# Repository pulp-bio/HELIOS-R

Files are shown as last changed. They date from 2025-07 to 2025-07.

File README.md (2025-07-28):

# HELIOS-R

## Handheld Embedded Laser diode Illumination for Optoacoustic – Ring shaped

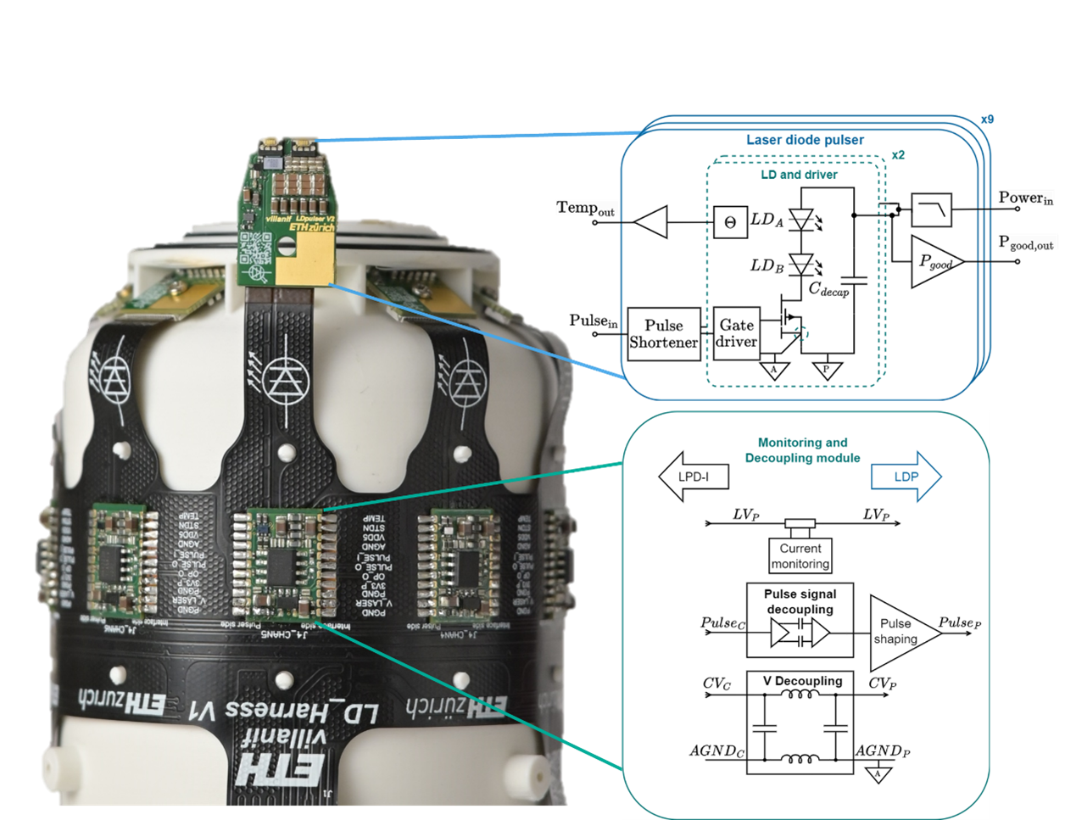
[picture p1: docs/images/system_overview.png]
System_overview


## Introduction

This repository contains the electronics design files for the HELIOS-R (Handheld Embedded Laser diode Illumination for Optoacoustic – Ring shaped) system. Helios-R is a high-current laser diode pulser array capable of delivering synchronized 100 ns light pulses at peak currents up to 2.88 kA at 22V, with a total light energy emission of up to 18 kW for up to 200 ns pulse widths.

The system drives a total of 144 laser diodes (9 pulser PCBs with 4 laser modules containing 4 laser diodes each) for optoacoustic imaging applications, featuring nanosecond-scale pulse generation with minimal electromagnetic interference in a compact, portable form factor.

## System Features

- **High-Current Pulsing**: 320 A per module, 2.88 kA total peak current capability
- **Nanosecond Timing**: Pulse shortening and pulse synchronization circuits for accurate timing control
- **Low EMI Design**: Advanced decoupling and filtering for minimal electromagnetic interference
- **Modular Architecture**: 9 independent pulser modules with monitoring and control

## System Architecture

The HELIOS-T electronics comprise four main PCB modules designed for optoacoustic imaging applications:

### Core Modules

1. **Laser Diode Pulser** (`ld_pulser`): High-current dual-channel GaN FET-based pulser with 4 laser diode modules, delivering 320 A at 22V pulse current. 
2. **Interconnect Harness** (`ld_harness`): Flexible PCB harness connecting all 9 pulsers with mechanical alignment and power distribution
3. **Monitoring & Decoupling** (`ld_monitoring_decoupling`): PI filter-based decoupling modules reduce EMI, featuring digital isolation and high-side current monitoring
4. **System Control** (`ld_system_control`): Interface PCB providing access to real-time monitoring of pulse duration, current consumption, and temperature



### Development & Testing

1. **Pulser Test Board** (`ld_pulser_testboard`): Standalone testing platform for pulser validation

## Repository Structure

This repository is organized as follows:

```text
HELIOS-R/
├── ld_pulser/                    # High-current laser diode pulser module
├── ld_system_control/           # Main system control unit
├── ld_monitoring_decoupling/    # Monitoring and signal conditioning
├── ld_harness/                 # Interconnection harness
├── ld_pulser_testboard/       # Standalone pulser test platform
├── shared/                   # Shared component libraries
│   └── lib/                 # Schematic and PCB component libraries
├── 3d_models/               # 3D models and mechanical assemblies
│   └── multiboard_assembly/ # Complete system 3D assembly
└── HELIOS_R.DsnWrk          # Altium Designer workspace file
```

each pcb module folder is structured as follows:
```
   ├── Hardware/                # PCB design files
   ├── Draftsman/               # Assembly and manufacturing drawings
   ├── Documentation/           # Schematics, assembly docs, and manufacturing files
   ├── Settings/                # Output job and BOM configurations
   └── <module_name>.PrjPcb     # Altium Designer PCB project file
```

## Key Specifications

- **Operating Voltage**: 22 V high-power rail
- **Operating Current**: Peak draw of 2A per module 
- **Peak Current**: 320 A per pulser module (Decoupled and filtered on each pulser module to obtain maximum draw of 2A per module)
- **Pulse Width**: 10-200 ns with 10 ns rising edge. Pulse shortening circuits shorten the pulse width by approximately 100ns
- **Pulse repetition Frequency**: Up to 10 kHz, depending on temperature and pulse width
- **PCB Specifications summary**:  
  - ld_pulser module: 6-layer, 1 mm thick with 70 µm copper planes and blind vias
  - ld_system_control: 6-layer, 1.2 mm thick
  - ld_harness: 2 layer flexible PCB
  - ld_monitoring_decoupling: 4-layer, 1 mm thick
- **EMI Suppression**: >120 dB attenuation (150 kHz - 280 MHz) via PI filtering
- **Decoupling Network**: 60 capacitors per module (47 nF, 2.2 µF, 10 µF stages)

## Getting Started

### Prerequisites for Development

- Altium Designer (recommended version 24.0 or later)

### Viewing the Design Files

1. **Open the workspace**:

   ```text
   Open HELIOS_R.DsnWrk in Altium Designer
   ```

2. **Navigate the projects**:
   - Each subsystem is organized as a separate Altium project
   - Hardware files contain schematics (.SchDoc) and PCB layouts (.PcbDoc)
   - Draftsman files contain assembly drawings and other information (.PCBDwf)

3. **Generate documentation**:
   - Use the provided OutJob files in each Settings folder
   - Generate PDFs, Gerber files, and BOMs as needed

## Manufacturing and Assembly

### PCB Fabrication

Each module includes complete manufacturing data:

- **Gerber Files**
- **Drill Files**
- **Pick & Place**: Component placement data for assembly
- **Bill of Materials (BOM)**

## Documentation

Comprehensive documentation is generated for each module:

- **Schematics**: Complete electrical schematics in PDF format
- **<project>_FULL_DOC.pdf**: Schematic, Fabrication and assembly instructions and component placement
- **Manufacturing Files**: fabrication and assembly data packages
- **BOMs**: Bill of materials with supplier information

Access documentation in the `Documentation/` folder of each project.

## Testing and Validation

Using the Pulser test board, pulsers can be tested individually by connecting them with a standard 18 pin, 0.5 mm pitch FPC cable.

## Safety Considerations

⚠️ **WARNING**: This system delivers extremely high energy light pulses. The system can only be operated in a laser-safe environment by safety-trained personnel. Exercise extreme caution and always follow safety protocols.
Please take note of the limitation of liability below [LIMITATION OF LIABILITY](#Limitation-of-Liability)

## Usage

1. connect a 22V, minimum 2A power supply (higher current required for faster pulse rates) to the banana plugs J6 and J5 on the back of the System Control module
2. Connect a 5V power supply to screw connector J10
3. Connect a signal generator (50 ohm, V_low = 0V, V_high = 5V) to the SMA connector J9 on the System Control module
4. Set a pulse width of 110 ns - 300 ns (the pulse width is shortened by approximately 100 ns by the pulse shortening circuit)
5. Set the pulse repetition frequency

The system can operate with a Laser diode supply voltage of up to 24V. It is reccomended to first enable the 5V power supply, then the Laser diode supply. 

## Contributing

This is an open hardware project. Contributions are welcome in the form of:

- Design improvements and optimizations
- Documentation enhancements
- Bug reports and fixes

## License

This project is released the Solderpad v0.51 open hardware license. See individual license files for specific terms:

- **Hardware Design Files**: Solderpad v0.51 (`SHL-0.51`) (see `LICENSE`)
- **Documentation and images**: Creative Commons Attribution 4.0 International License (`CC-BY-4.0`) (see `docs/LICENSE_CC`):

## Authors and Acknowledgments

The HELIOS-R PCB System was developed by the IIS laboratory at ETH Zurich by Federico Villani (System architecture, simulation, design and layout), based on requirements and the concept of handheld optoacoustic imaging by Xiang Liu and Prof. Daniel Razansky. 

The PCB system is part of a wider effort, the paper **Laser diode-based large-scale compounding handheld volumetric optoacoustic tomography**, with following summarized contributions (for the full list of contributions, please refer to the paper): 

- **Xiang Liu**:  Conceptualization, methodology, investigation, experimentation, software & data analysis, visualization, writing
- **Federico Villani**: PCB system design, methodology, investigation, writing
- **Isaac Esteban Varela**: Software & data analysis
- **Xuyang Chang** & **Baoyuan Zhang**: Investigation, experimentation
- **Andrea Cossettini**: Investigation, writing
- **Xose Luis Dean-Ben**: Software & data analysis, writing  
- **Luca Benini** & **Daniel Razansky**: Conceptualization, project administration, supervision, writing

```
@article{liuHandheldEmbeddedLaserDiode,
  title = {Handheld {{Embedded Laser-Diode Illumination Optoacoustic System}} for {{Real-Time 3D Angiography}} of {{Deep Tissues}}},
  author = {Liu, Xiang and Villani, Federico and Esteban, Isaac and Chang, Xuyang and Zhang, Baoyuan and Cossettini, Andrea and {De{\'a}n-Ben}, Xos{\'e} Lu{\'i}s and Benini, Luca and Razansky, Daniel},
  journal = {Laser \& Photonics Reviews},
  volume = {n/a},
  number = {n/a},
  pages = {e01006},
  issn = {1863-8899},
  doi = {10.1002/lpor.202501006},
  urldate = {2025-07-28},
  copyright = {{\copyright} 2025 The Author(s). Laser \& Photonics Reviews published by Wiley-VCH GmbH},
  langid = {english},
  keywords = {Compact,Handheld,Laser diode,Low cost,Nir wavelength,Optoacoustic Tomography,Photoacoustic,Vasculature}
}

```

Pictures of the system by: Federico Villani, Sergei Vostrikov, Xiang Liu.

## Contact and Support

For technical questions or design collaboration inquiries:

- Open an issue in this repository for technical discussions
- Contact us for collaboration opportunities

## Limitation of Liability

In no event and under no legal theory, whether in tort (including negligence), contract, or otherwise, unless required by applicable law (such as deliberate and grossly negligent acts) or agreed to in writing, shall any Contributor be liable to You for damages, including any direct, indirect, special, incidental, or consequential damages of any character arising as a result of this License or out of the use or inability to use the Work (including but not limited to damages for loss of goodwill, work stoppage, computer failure or malfunction, or any and all other commercial damages or losses), even if such Contributor has been advised of the possibility of such damages.

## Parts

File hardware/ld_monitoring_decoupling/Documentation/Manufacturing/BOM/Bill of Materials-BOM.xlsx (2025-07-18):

Line # | Name | Description | Designator | Footprint | LibRef | Supplier 1 | Supplier Part Number 1 | Quantity
 | 0 | RES SMD 0OHM 0.1% 1/20W 0201 | R4, R5 | RES 0201_0603 | ERJ-1GN0R00C | Mouser | 667-ERJ-1GN0R00C | 2
 | 0 | RES SMD 0OHM 1/10W 0402 | R7, R8 | RES 0402_1005 | ERJ-S020R00X | Mouser | 667-ERJ-S020R00X | 2
 | 0.1uF | CAP CER 0.1UF 35V X5R 0201 | C1, C2, C9, C10 | CAP 0201_0603 | GRM033R6YA104ME14D | Mouser | 81-GRM33R6YA104ME14D | 4
 | 1 kOhms @ 100 MHz | FERRITE BEAD 1K OHM 0603 1LN | FB1, FB2, FB3, FB4 | FER 0603_1608 | BLM18SP102SH1D | DigiKey | 490-BLM18SP102SH1DCT-ND | 4
 | 1uF | CAP LOW L CER 1UF 6.3V X7T 0204 | C4, C5, C6, C7, C13 | FP-LLL152-0_2-MFG | LLL152D70J105ME01D | Mouser | 81-LLL152D70J105ME01 | 5
 | 10k | RES SMD 10KOHM 0.1% 63mW 0402 | R3 | RES 0402_1005 | ERJ-1GNF1002C | Mouser | 667-ERA-2AEB103X | 1
 | 24 | RES SMD 24 OHM 1% 1/20W 0201 | R11 | RES 0201_0603 | ERJ-1GNF24R0C | Mouser | 667-ERJ-1GNF24R0C | 1
 | 200m | RES 0.2 OHM 1% 1/5W 0603 | R6 | STACKPOLE CSR0603 | RL0816S-R20-F | DigiKey | 408-1479-1-ND | 1
 | INA139NA_3K | IC Inamp high-side current monitor | U1 | SOT95P280X145-5N | INA139NA_3K | Mouser | 595-INA139NA/3K | 1
 | MAX22291CASA_V+ | IC Digital Isolator, 2CH | U2 | SOIC127P600X175-8N | MAX22291CASA_V+ | Mouser | 700-MAX22291CASA/V+ | 1
2 | 20 pF | CAP CER 20PF 50V C0G/NP0 0402 | C11, C12 | CAP 0402_1005 | GCM1555C1H200FA16D | DigiKey | 490-GCM1555C1H200FA16DCT-ND | 2
3 | 4.7uF | CAP CER 4.7UF 50V X6S 0805 | C3, C8, C14, C15 | CAP 0805_2012 | GRM21BC81H475KE11L | Mouser | 81-GRM21BC81H475KE1K | 4
18 | 4.99 k | RES SMD 4.99KOHM 0.1% 1/16W 0402 | R1, R2 | RES 0402_1005 | ERA-2AEB4991X | DigiKey | 10-ERA-2AEB4991XCT-ND | 2
23 | 4.99 k | RES SMD 4.99 kOHM 1% 1/20W 0201 | R9, R10 | RES 0201_0603 | ERJ-1GNF4991C | Mouser | 667-ERJ-1GNF4991C | 2
27 | SN74LVC1G08YZPR | IC Single 2-Input Positive-AND Gate, YZP0005ADAD, LARGE T&R | U3 | YZP0005ADAD | SN74LVC1G08YZPR | Mouser | 595-SN74LVC1G08YZPR | 1

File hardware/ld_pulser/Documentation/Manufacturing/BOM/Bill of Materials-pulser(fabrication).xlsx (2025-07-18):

Line # | Name | Description | Designator | Footprint | LibRef | Supplier 1 | Supplier Part Number 1 | Quantity
1 | 0.1uF | CAP CER 0.1UF 35V X5R 0201 | C1, C3, C5, C6, C7, C15 | CAP 0201_0603 | GRM033R6YA104ME14D | Digi-Key | 490-10431-1-ND | 6
2 | 20 pF | CAP CER 20PF 50V C0G/NP0 0402 | C2 | CAP 0402_1005 | GCM1555C1H200FA16D | Digi-Key | 490-GCM1555C1H200FA16DCT-ND | 1
3 | 10uF | CAP CER 10UF 25V X5R 0603 | C4, C13, C14, CC_1_1, CC_1_2, CC_1_3, CC_1_4, CC_1_5, CC_1_6, CC_2_1, CC_2_2, CC_2_3, CC_2_4, CC_2_5, CC_2_6 | CAP 0603_1608 | ZRB18AR61E106ME01L | Mouser | 81-ZRB18AR61E106ME1L | 15
4 | 2.2 µF | CAP CER 2.2UF 50V X5R 0603 | C_1_8, C_2_8, CB_1_1, CB_1_2, CB_1_3, CB_1_4, CB_1_5, CB_1_6, CB_1_7, CB_1_8, CB_1_9, CB_1_10, CB_1_11, CB_1_12, CB_2_1, CB_2_2, CB_2_3, CB_2_4, CB_2_5, CB_2_6, CB_2_7, CB_2_8, CB_2_9, CB_2_10, CB_2_11, CB_2_12 | CAP 0603_1608 | GRM188R61H225KE11D | Mouser | 81-GRM188R71A225KE15 | 26
5 | NFM15PC474R0J3D | CAP Feed Through, 470 nF, 6.3V, 2A, 3 Pin(s) | C_1_9, C_2_9 | FP-NFM15-0_05-MFG | NFM15PC474R0J3D | Mouser | 81-NFM15PC474R0J3D | 2
6 | 47 nF | CAP CER 47 nF, 50V, 20% X7R 0204 | C_1_10, C_2_10, CA_1_1, CA_1_2, CA_1_3, CA_1_4, CA_1_5, CA_1_6, CA_1_7, CA_1_8, CA_1_9, CA_1_10, CA_1_11, CA_1_12, CA_1_13, CA_1_14, CA_1_15, CA_2_1, CA_2_2, CA_2_3, CA_2_4, CA_2_5, CA_2_6, CA_2_7, CA_2_8, CA_2_9, CA_2_10, CA_2_11, CA_2_12, CA_2_13, CA_2_14, CA_2_15 | CAPC0510X35N | CGAEA1X7R1H473M030BC | Mouser | 810-CGAEA1X7R1H473M0 | 32
7 | 1uF | CAP LOW L CER 1UF 6.3V X7T 0204 | C_1_11, C_2_11 | FP-LLL152-0_2-MFG | LLL152D70J105ME01D | Mouser | 81-LLL152D70J105ME01 | 2
8 | 33nF | CAP LOW L CER 33nF 25V X5R 0102 | C_1_12, C_2_12 | FP-LLL03T-0_03-IPC_C | LLL03TR61E333KE01 | Mouser | 81-LLL03T61E333KE01L | 2
9 | SPL_S4L90A_3_A01 | Diode Laser | D_1_1, D_1_2, D_2_1, D_2_2 | SPLS4L90A_3A01 | SPL_S4L90A_3_A01 | Mouser | 720-SPLS4L90A3A01 | 4
10 | APG0603SEC-E-TT | Diode LED RED 10 mA @ 1.93 V lv=40 | LED1 | APG0603SECETT | APG0603SEC-E-TT | Mouser | 604-APG0603SECETT | 1
11 | APG0603VBC-A1-5MAV | Diode LED BLUE 10 mA @ 2.9 V lv=60 | LED2 | APG0603SECETT | APG0603VBC-A1-5MAV | Mouser | 604-APG0603VBCA15MAV | 1
12 | APG0603ZGC-5MAV | Diode LED GREEN 5 mA @ 2.85 V lv=80(?) | LED3 | APG0603SECETT | APG0603ZGC-5MAV | Mouser | 604-APG0603ZGC-5MAV | 1
13 | =Value | FERRITE BEAD 100 OHM 0603 1LN | FB1, FB2 | FER 0603_1608 | BLM18SP101SN1 | Mouser | 81-BLM18SP101SN1D | 2
14 | NFL18ZT506H1A3D | LC Filter | FL_1_1, FL_2_1 | NFL18ST107H1A3D | NFL18ZT506H1A3D | Mouser | 81-NFL18ZT506H1A3D | 2
15 | EPC2619ENGRT | Transistor eGaN | Q_1_1, Q_2_1 | EPC2619ENGRT | EPC2619ENGRT | Digi-Key | 917-EPC2619ENGRTCT-ND | 2
16 | 51 | RES SMD 51 OHM 1% 1/20W 0201 | R3 | RES 0201_0603 | ERJ-1GNF51R0C | Mouser | 667-ERJ-1GNF51R0C | 1
17 | 4.99 k | RES SMD 4.99KOHM 0.1% 1/16W 0402 | R2, R12 | RES 0402_1005 | ERA-2AEB4991X | Digi-Key | 10-ERA-2AEB4991XCT-ND | 2
18 | 470 | RES SMD 470 OHM 1% 1/20W 0201 | R1, R4 | RES 0201_0603 | ERJ-1GNF4991C_1 | Mouser | 667-ERJ-1GNF4700C | 2
19 | 1 M | RES SMD 1MOHM 1% 1/20W 0201 | R6 | RES 0201_0603 | ERJ-U01F1004C | Mouser | 667-ERJ-U01F1004C | 1
20 | 100k | RES SMD 100 kOHM 0.5% 1/20W 0201 | R7 | RES 0201_0603 | ERJ-1RHD1003C | Mouser | 667-ERJ-1RHD1003C | 1
21 | LM94023BITME_NOPB | IC temperature sensor | U1 | BGA4C40P2X2_81X81X68 | LM94023BITME_NOPB | Mouser | 926-94023bitME/NOPB | 1
22 | 4.99 k | RES SMD 4.99 kOHM 1% 1/20W 0201 | R9 | RES 0201_0603 | ERJ-1GNF4991C | Mouser | 667-ERJ-1GNF4991C | 1
23 | 2 | RES SMD 2 OHM 1% 1/20W 0201 | R_1_10, R_1_11, R_2_10, R_2_11 | RES 0201_0603 | ERJ-1GNJ2R0C | Mouser | 667-ERJ-1GNJ2R0C | 4
24 | MAX40007ANT+ | Operational Amplifier | U4 | BGA6C40P3X2_124X84X69 | MAX40007ANT+ | Mouser | 700-MAX40007ANT+T | 1
25 | 503480-1800 | Conn FPC 18 POS 0.5mm | J1 | 5034801800 | 503480-1800 | Mouser | 538-503480-1800 | 1
26 | SN74LVC1G08YZPR | IC Single 2-Input Positive-AND Gate, YZP0005ADAD, LARGE T&R | U2 | YZP0005ADAD | SN74LVC1G08YZPR | Mouser | 595-SN74LVC1G08YZPR | 1
28 | SN74LVC1G06YZPR | IC Single Inverter Buffer/Driver With Open-Drain Output, YZP0005ADAD, LARGE T&R | U7 | YZP0005ADAD | SN74LVC1G06YZPR | Mouser | 595-SN74LVC1G06YZPR | 1
29 | LMG1020YFFR | IC Pulser | U_1_6, U_2_6 | BGA6C40P2X3_86X126X62 | LMG1020YFFR | Mouser | 595-LMG1020YFFR | 2

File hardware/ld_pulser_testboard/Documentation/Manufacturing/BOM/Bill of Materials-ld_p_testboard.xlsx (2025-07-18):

Name | Description | Designator | Footprint | LibRef | Supplier 1 | Supplier Part Number 1 | Quantity | Line #
10 µF | CAP CER 10UF 100V X7S 1210 | C1, C2 | CAP 1210_3225 - 1MM | GRM32EC72A106ME05L | Digi-Key | 490-GRM32EC72A106ME05LCT-ND | 2 | 4
503480-2400 | Connector | J1 | 5034802400 | 503480-2400 | Mouser | 538-503480-2400 | 1 | 6
282834-2 | TERM BLK 2P SIDE ENT 2.54MM PCB | J2, J3, J9 | TE 282834-2 | 282834-2 | Digi-Key | A98333-ND | 3 | 9
1470510-1 | SMA Connector Jack, Female Socket 50 Ohm Through Hole Solder | J4, J5, J6, J8 | 5-1814832-1 | CMP-00606-1 |  |  | 4 | 8
M20-7820342 | CONN RCPT 3POS 0.1 GOLD PCB | J7 | HARWIN M20-7820345 | M20-7820342 | Digi-Key | 952-1783-ND | 1 | 5
51 | RES SMD 51 OHM 1% 1/20W 0201 | R1, R2 | RES 0201_0603 | ERJ-1GNF51R0C | Mouser | 667-ERJ-1GNF51R0C | 2 | 7
TPSM265R1V3SILR | 3-V TO 65-V INPUT, 100-MA, STEP- | U1 | FP-SIL0010C-MFG | TPSM265R1V3SILR | Mouser | 595-TPSM265R1V3SILR | 1
68000-102HLF | 2 Positions Header, Unshrouded Connector 0.100" (2.54mm) Through Hole Gold or Gold, GXT™ | X1, X2, X3, X6, X8 | 68000-102HLF | CMP-00100-3 | Arrow Electronics | 68000-102HLF | 5 | 1
68000-102HLF | 2 Positions Header, Unshrouded Connector 0.100" (2.54mm) Through Hole Gold or Gold, GXT™ | X4, X5, X7, X9 | 68000-102HLF | CMP-00100-3_1 | Arrow Electronics | 68000-102HLF | 4 | 2

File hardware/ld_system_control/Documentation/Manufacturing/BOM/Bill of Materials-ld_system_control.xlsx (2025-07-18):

Name | Description | Designator | Footprint | LibRef | Supplier 1 | Supplier Part Number 1 | Quantity | Line #
10 µF | CAP CER 10UF 100V X7S 1210 | C1, C2 | CAP 1210_3225 - 1MM | GRM32EC72A106ME05L | Digi-Key | 490-GRM32EC72A106ME05LCT-ND | 2 | 4
200528-0140 | FFC / FPC Board Connector, 1 mm, 14 Contacts, Receptacle, Easy-On 52207 Series, Surface Mount | J1 | 200528-0140 | 522071460 | Mouser | 538-52207-1460 | 1
503480-1800 | Conn FPC 18 POS 0.5mm | J2, J3 | 5034801800 | 503480-1800 | Mouser | 538-503480-1800 | 2
M20-7820342 | Header 3 Positions, Unshrouded Connector 0.100" (2.54mm) Through Hole Gold or Gold, GXT™ | J4, J8 | HARWIN M20-7820345 | M20-7820342 | DigiKey | 952-1783-ND | 2
CT3151-2 | Banana plug connector - Red | J5 | CT31510 | CT3151-2 | Mouser | 510-CT3151-2 | 1
CT3151-0 | Banana plug connector - Black | J6 | CT31510 | CT3151-0 | Mouser | 510-CT3151-0 | 1
1470510-1 | SMA Connector Jack, Female Socket 50 Ohm Through Hole Solder | J7, J9 | 5-1814832-1 | CMP-00606-1 |  |  | 2 | 8
282834-2 | TERM BLK 2P SIDE ENT 2.54MM PCB | J10 | TE 282834-2 | 282834-2 | DigiKey | A98333-ND | 1
WSL3637R0100DEA | current measurement Resistor | R1 | WSL3637R0100DEA | WSL3637R0100DEA | Mouser | 71-WSL3637R0100DEA | 1
51 | RES SMD 51 OHM 1% 1/20W 0201 | R2 | RES 0201_0603 | ERJ-1GNF51R0C | Mouser | 667-ERJ-1GNF51R0C | 1 | 7
TPSM265R1V3SILR | 3-V TO 65-V INPUT, 100-MA, STEP- | U1 | FP-SIL0010C-MFG | TPSM265R1V3SILR | Mouser | 595-TPSM265R1V3SILR | 1
68000-102HLF | Header 2 Positions , Unshrouded Connector 0.100" (2.54mm) Through Hole Gold or Gold, GXT™ | X1, X2, X4, X5 | 68000-102HLF | CMP-00100-3_1 |  |  | 4
68000-102HLF | Header 9*2 Positions, Unshrouded Connector 0.100" (2.54mm) Through Hole Gold or Gold, GXT™ | X6, X8 | TSW-109-07-G-D | 68000-102HLF |  |  | 2
68000-102HLF | Header 2 positions, Unshrouded Connector 0.100" (2.54mm) Through Hole Gold or Gold, GXT™ | X7 | 68000-102HLF | CMP-00100-3 |  |  | 1

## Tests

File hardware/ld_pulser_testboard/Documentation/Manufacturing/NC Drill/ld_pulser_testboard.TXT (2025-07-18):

M48
;Layer_Color=9474304
;FILE_FORMAT=4:4
METRIC,LZ
;TYPE=PLATED
T01F00S00C0.3000
T02F00S00C1.0200
T03F00S00C1.1000
T04F00S00C1.1000
T05F00S00C1.5000
T06F00S00C1.6000
T07F00S00C3.3000
%
T01
X002728Y000135
X002878
X002875Y000275
X002975
X003075
X003175
X003275
X003375
X00347246Y00026652
X00355746
X00364246
X00372746
X00381246
X00389746
X00398246
X00406746
X00415246
X00423746
X00432246
X00440746
X00449246
X00457746
X00466246
X00474746
X00483246Y00026701
X00488098Y0003368
Y0004218
Y0005068
Y0005918
Y0006768
Y0007618
Y0008468
Y0009318
Y0010168
X00505299Y000885
X00520299
X00535299
X00550299
X00542799Y000735
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

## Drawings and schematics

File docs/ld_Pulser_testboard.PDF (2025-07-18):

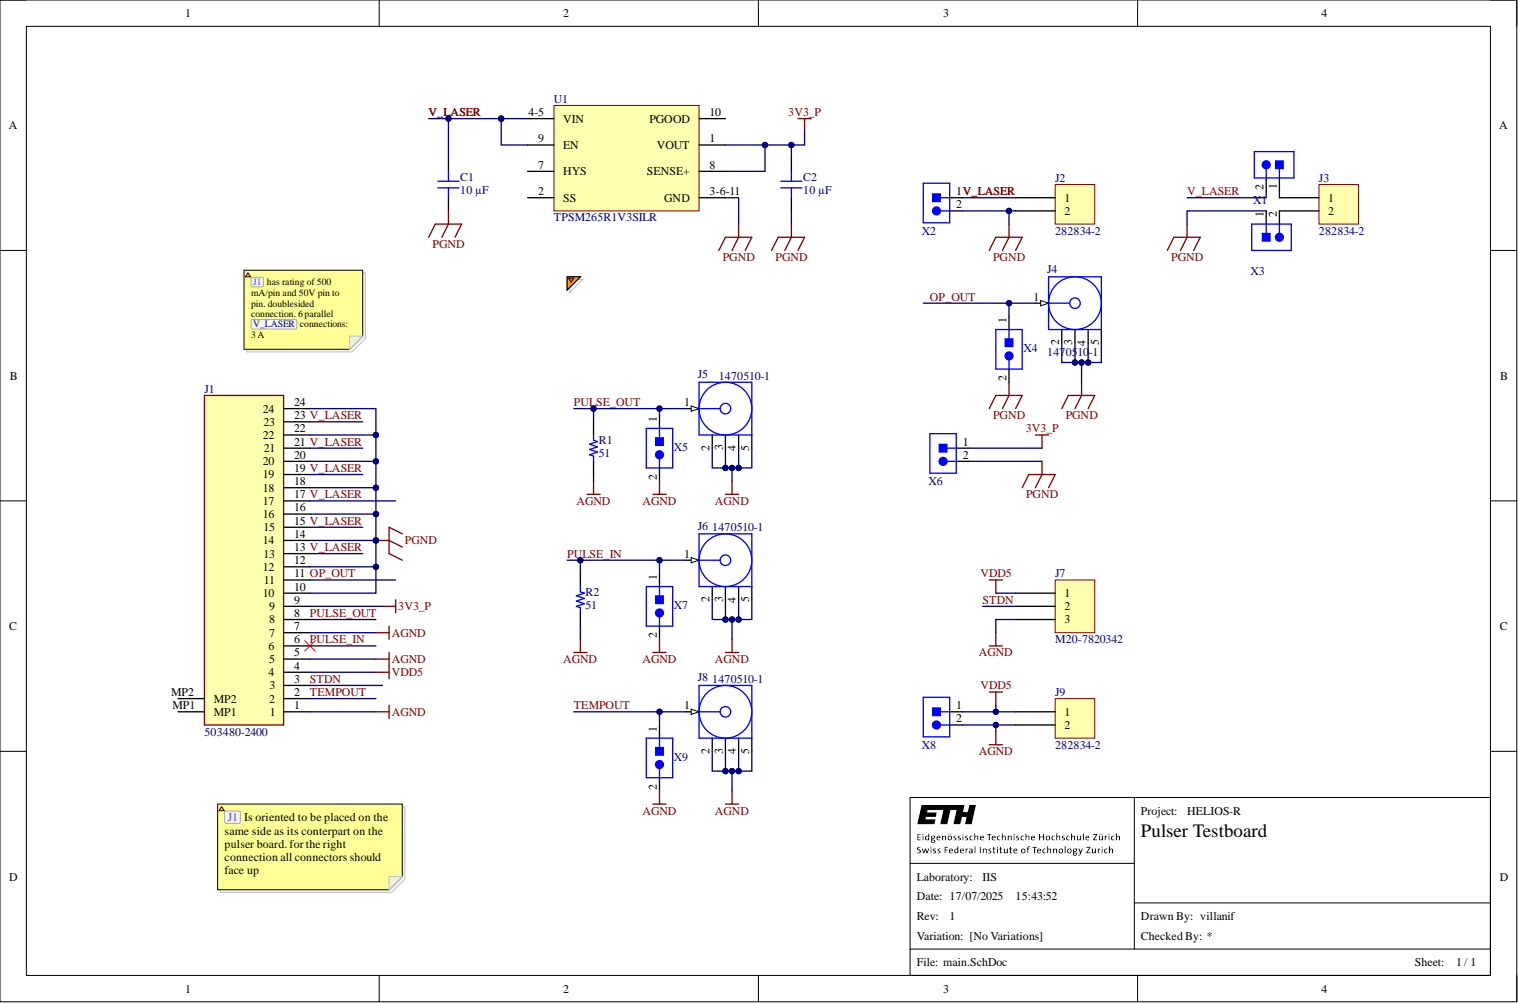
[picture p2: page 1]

2 3 2 2 | V _ L ASE R

2 1 2 0 | V _ L ASE R

1 9 1 8 | V _ L ASE R

1 7 | V _ L ASE R
1 6

1 3 1 2 | V _ L ASE

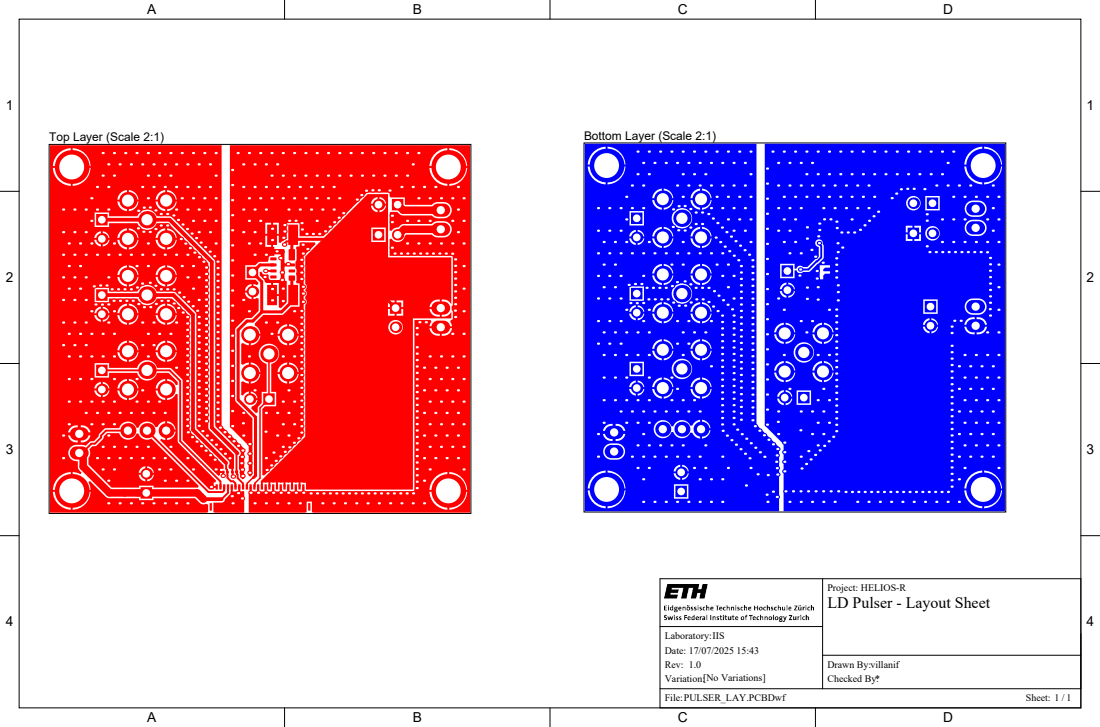
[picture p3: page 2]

Project: HELIOS-R
LD Pulser - Layout Sheet

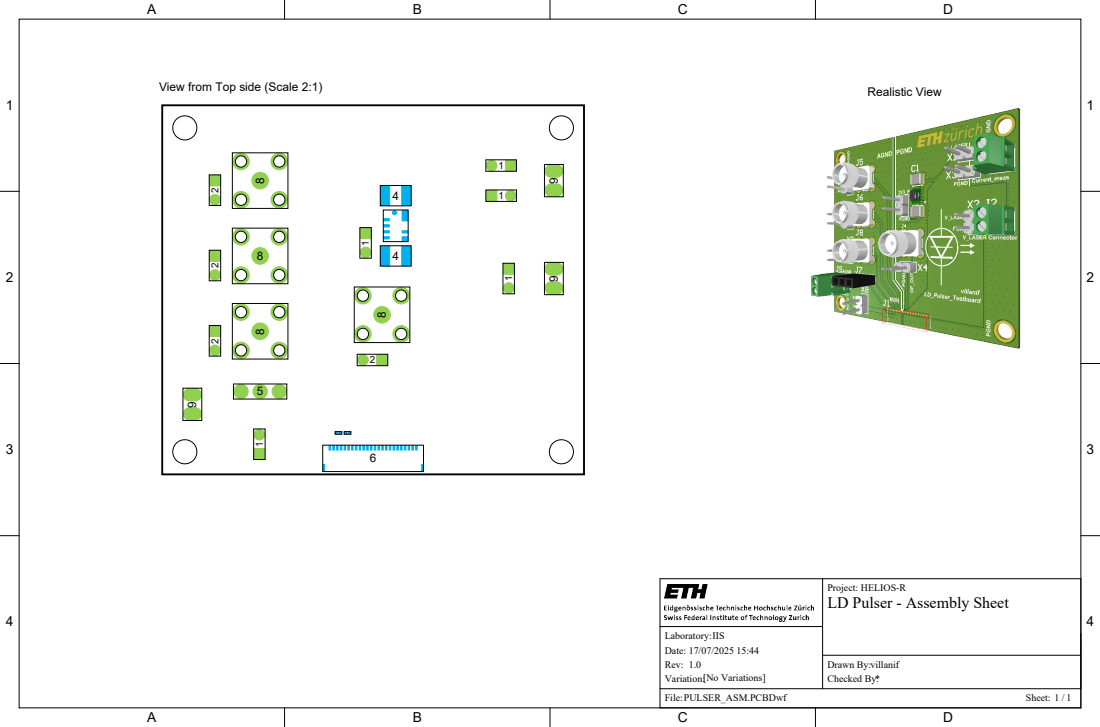
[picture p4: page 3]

View from Top side (Scale 2:1)

Project: HELIOS-R
LD Pulser - Assembly Sheet

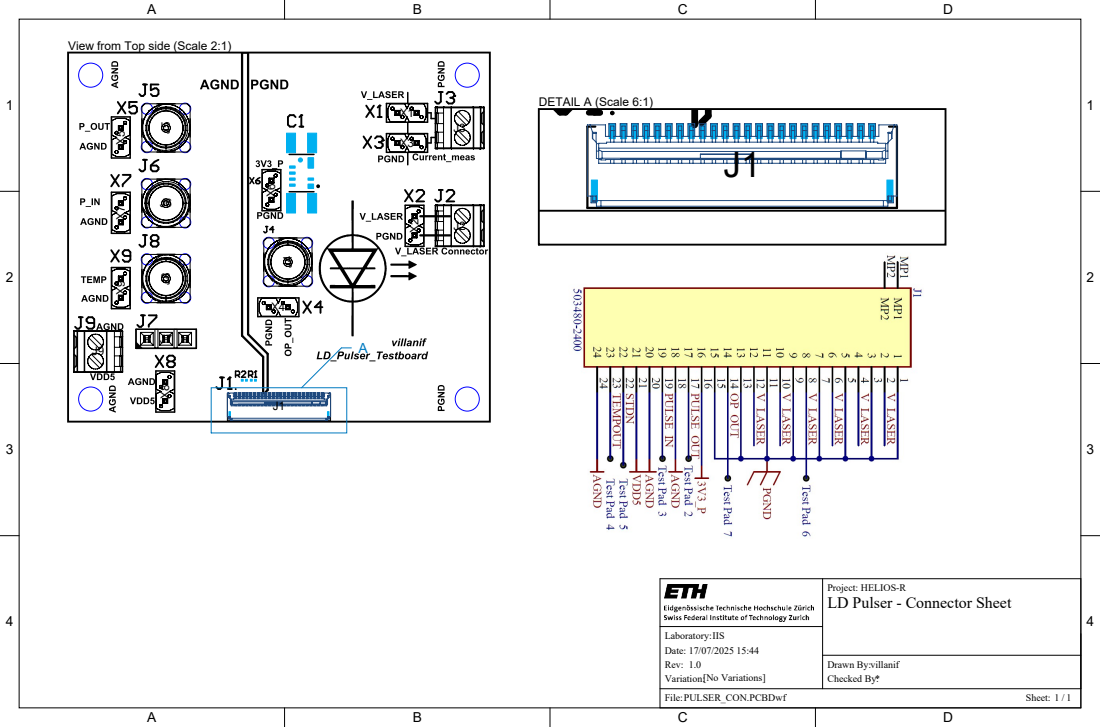
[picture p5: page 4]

View from Top side (Scale 2:1)

Project: HELIOS-R
LD Pulser - Connector Sheet

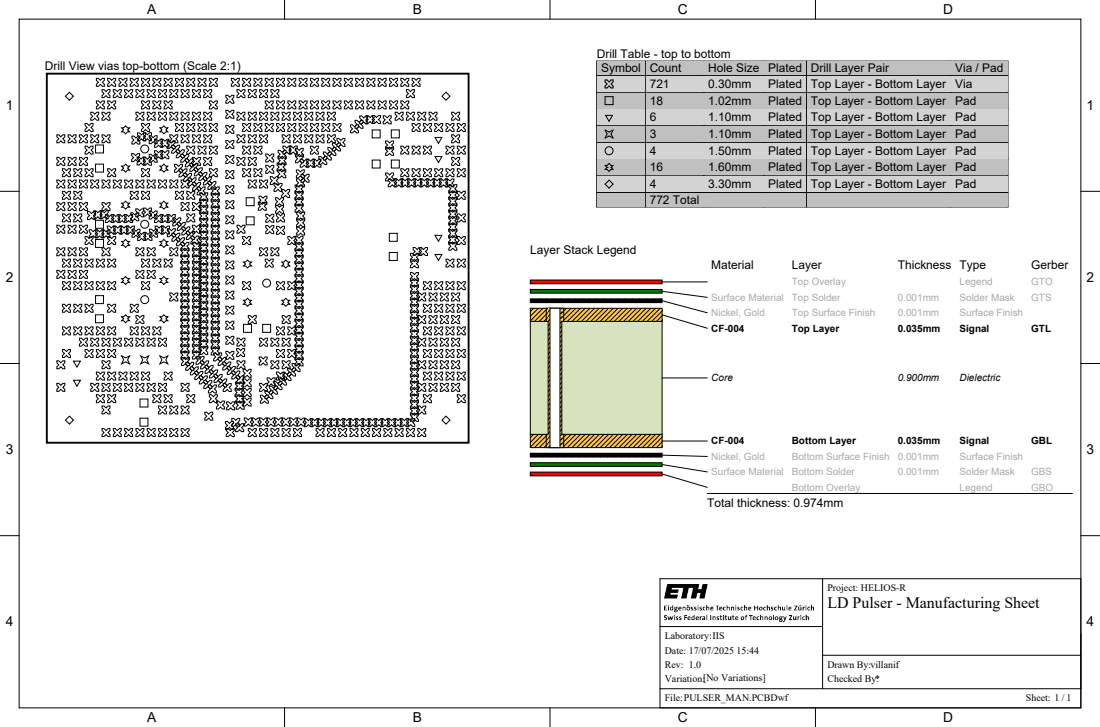
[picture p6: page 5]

Drill Table - top to bottom

Drill View vias top-bottom (Scale 2:1)

Symbol | Count | Hole Size | Plated | Drill Layer Pair | Via / Pad

721 | 0.30mm | Plated | Top Layer - Bottom Layer | Via
18 | 1.02mm | Plated | Top Layer - Bottom Layer | Pad
6 | 1.10mm | Plated | Top Layer - Bottom Layer | Pad
3 | 1.10mm | Plated | Top Layer - Bottom Layer | Pad
4 | 1.50mm | Plated | Top Layer - Bottom Layer | Pad
16 | 1.60mm | Plated | Top Layer - Bottom Layer | Pad
4 | 3.30mm | Plated | Top Layer - Bottom Layer | Pad
772 Total

Project: HELIOS-R
LD Pulser - Manufacturing Sheet

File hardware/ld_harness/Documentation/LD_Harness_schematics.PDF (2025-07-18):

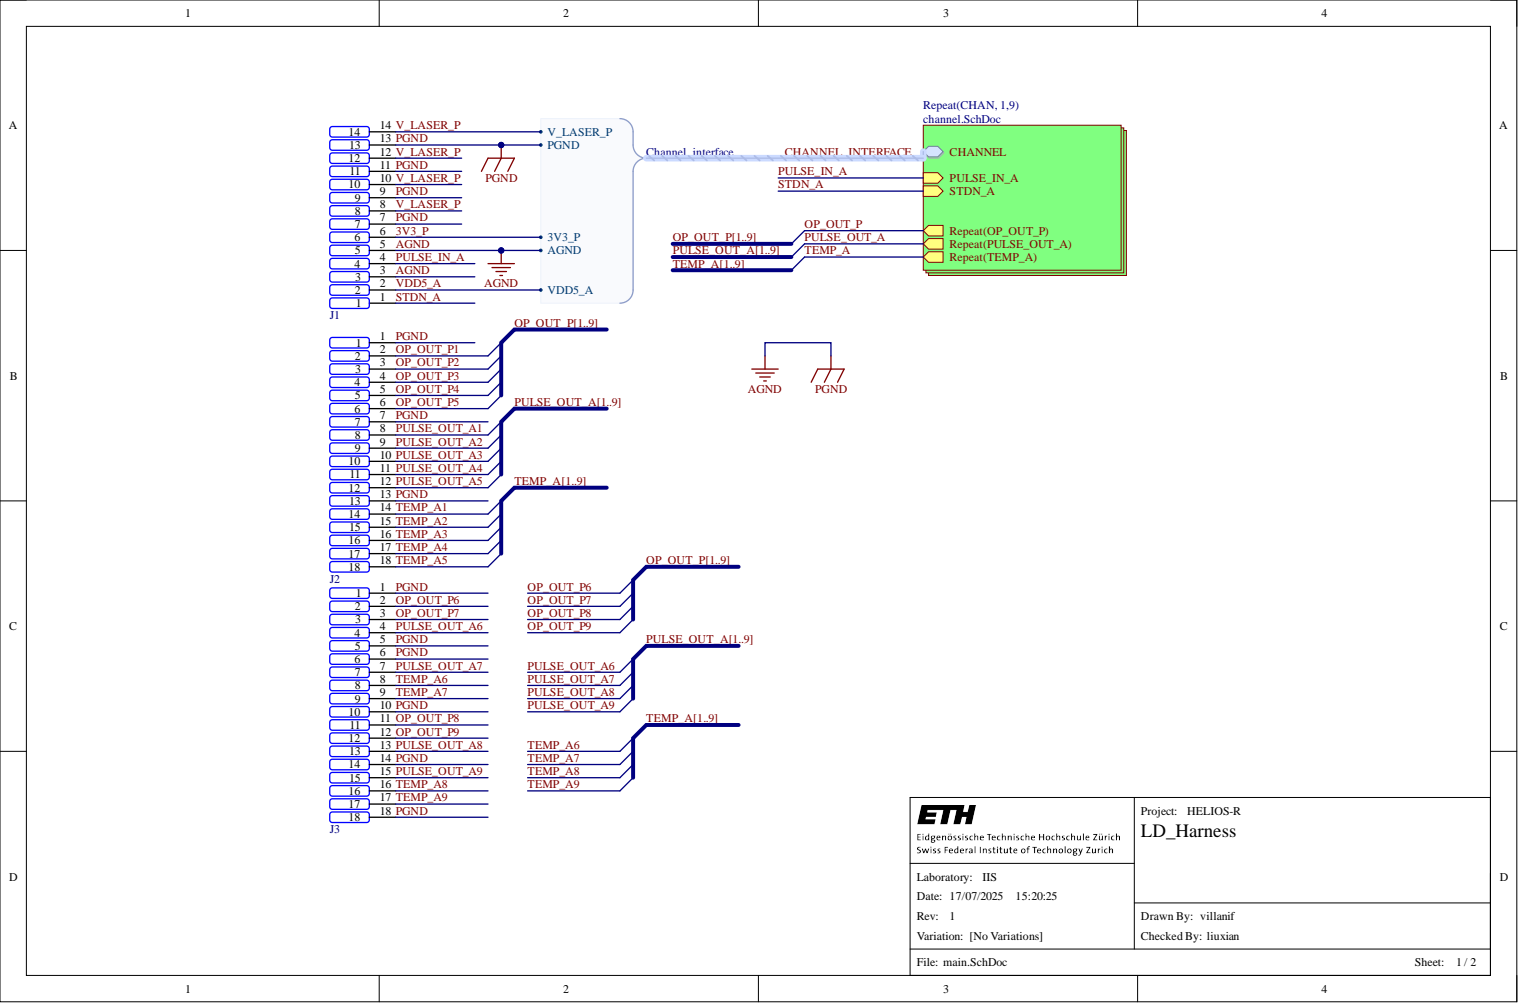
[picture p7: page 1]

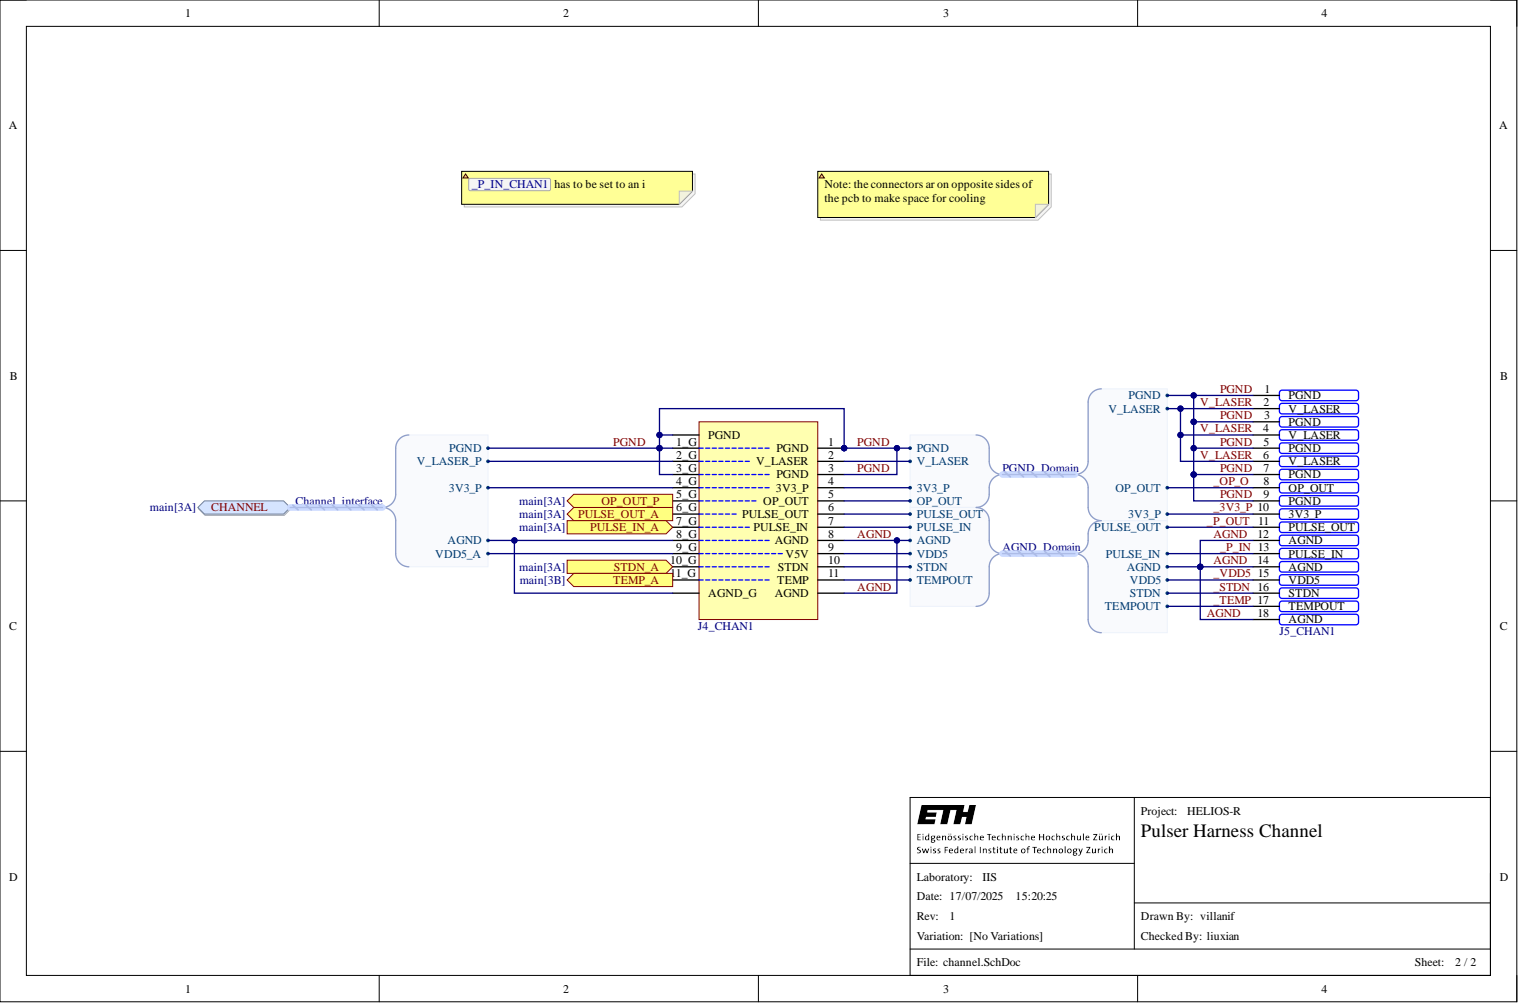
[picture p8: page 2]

_P_IN_CHAN1 has to be set to an i

Note: the connectors ar on opposite sides of
the pcb to make space for cooling

PGND

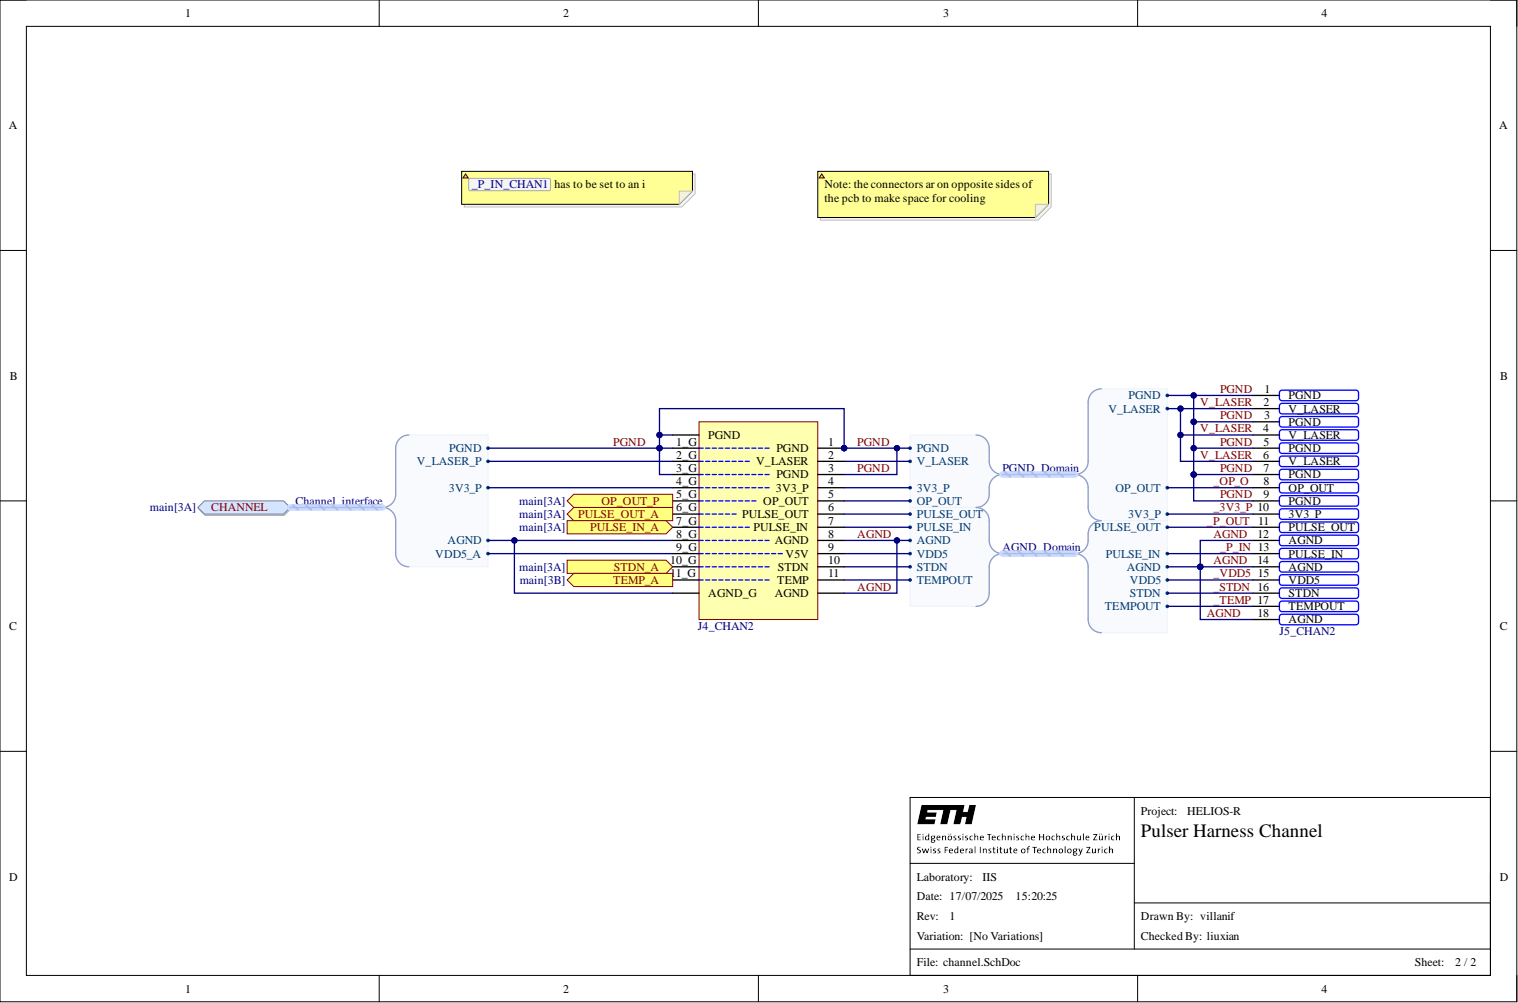
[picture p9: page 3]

_P_IN_CHAN1 has to be set to an i

Note: the connectors ar on opposite sides of
the pcb to make space for cooling

PGND

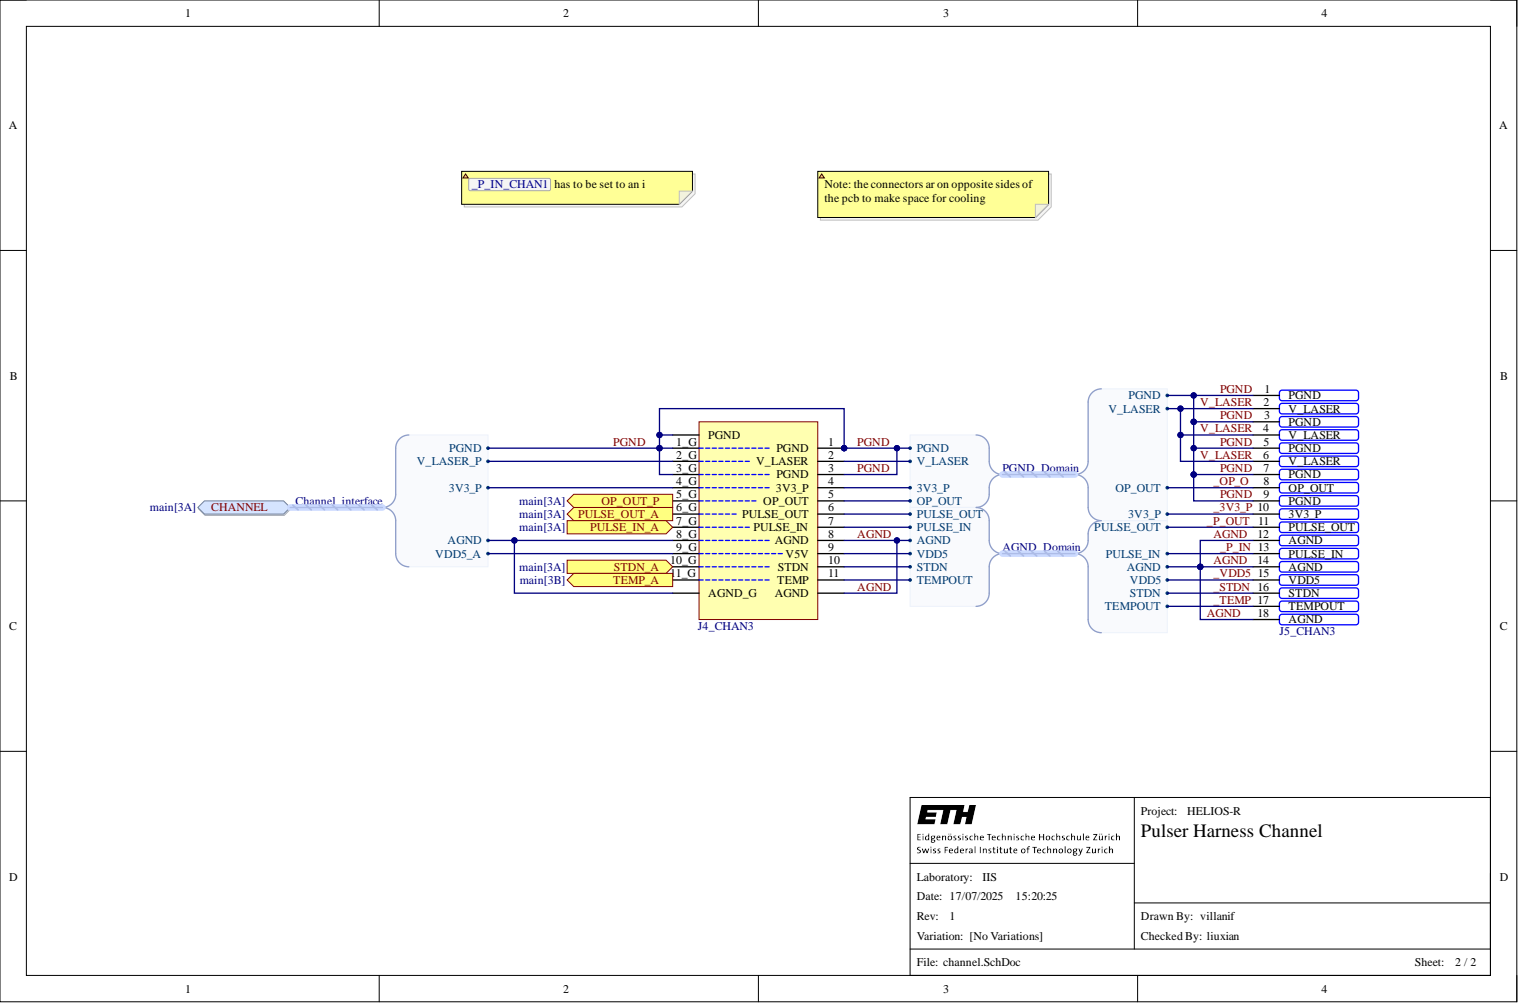
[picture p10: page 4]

_P_IN_CHAN1 has to be set to an i

Note: the connectors ar on opposite sides of
the pcb to make space for cooling

PGND

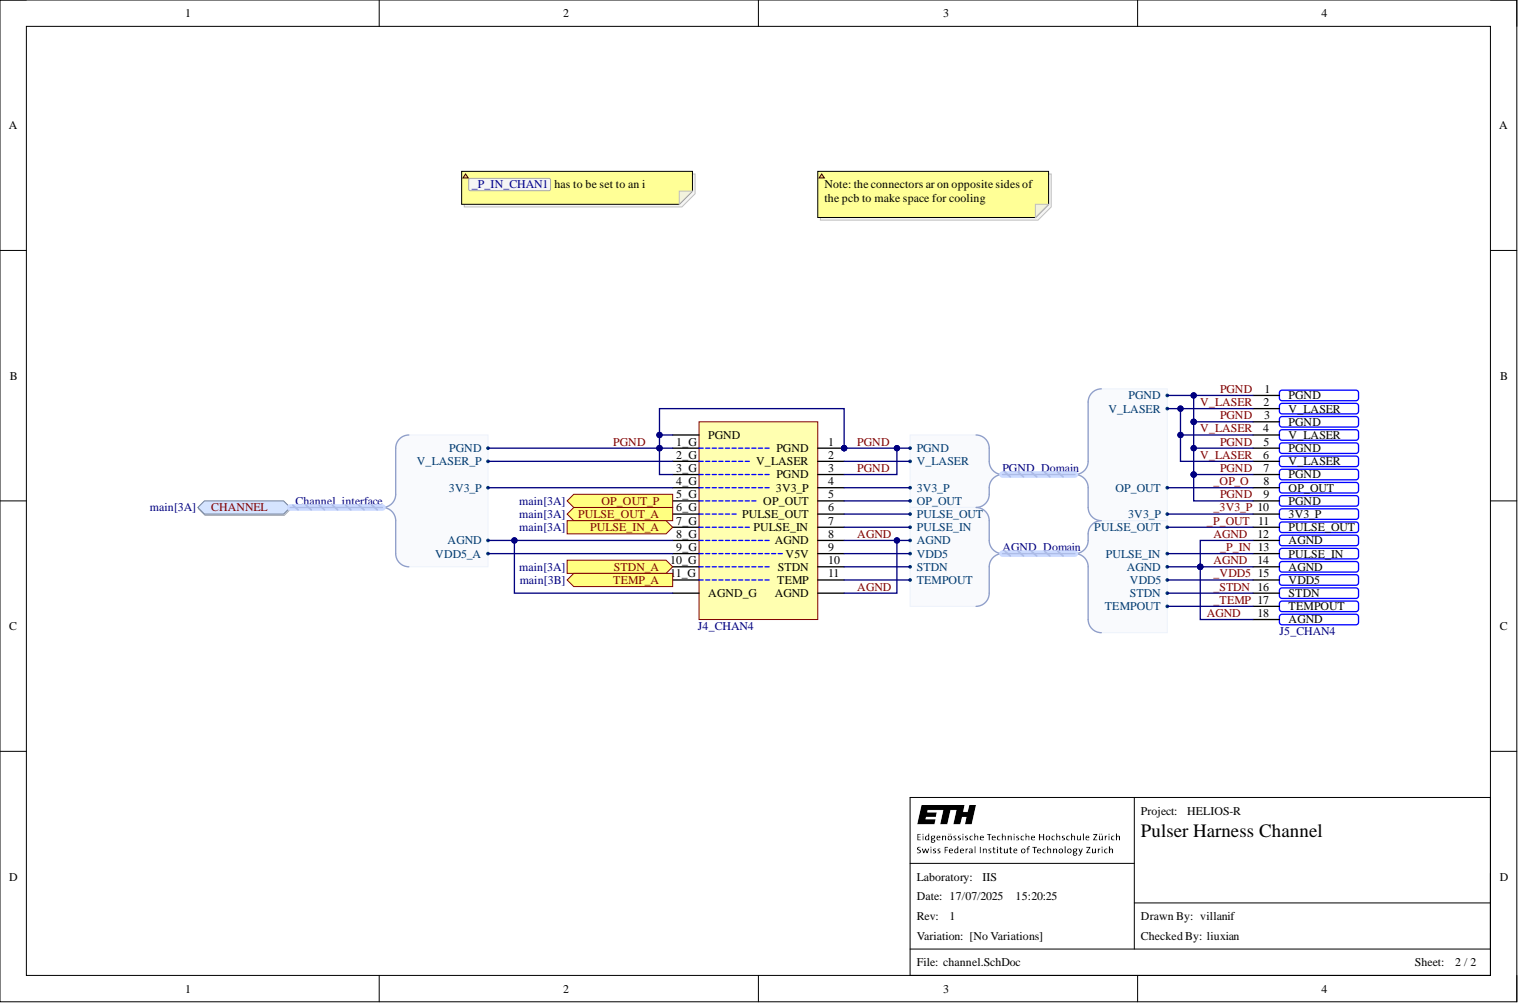
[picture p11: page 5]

_P_IN_CHAN1 has to be set to an i

Note: the connectors ar on opposite sides of
the pcb to make space for cooling

PGND

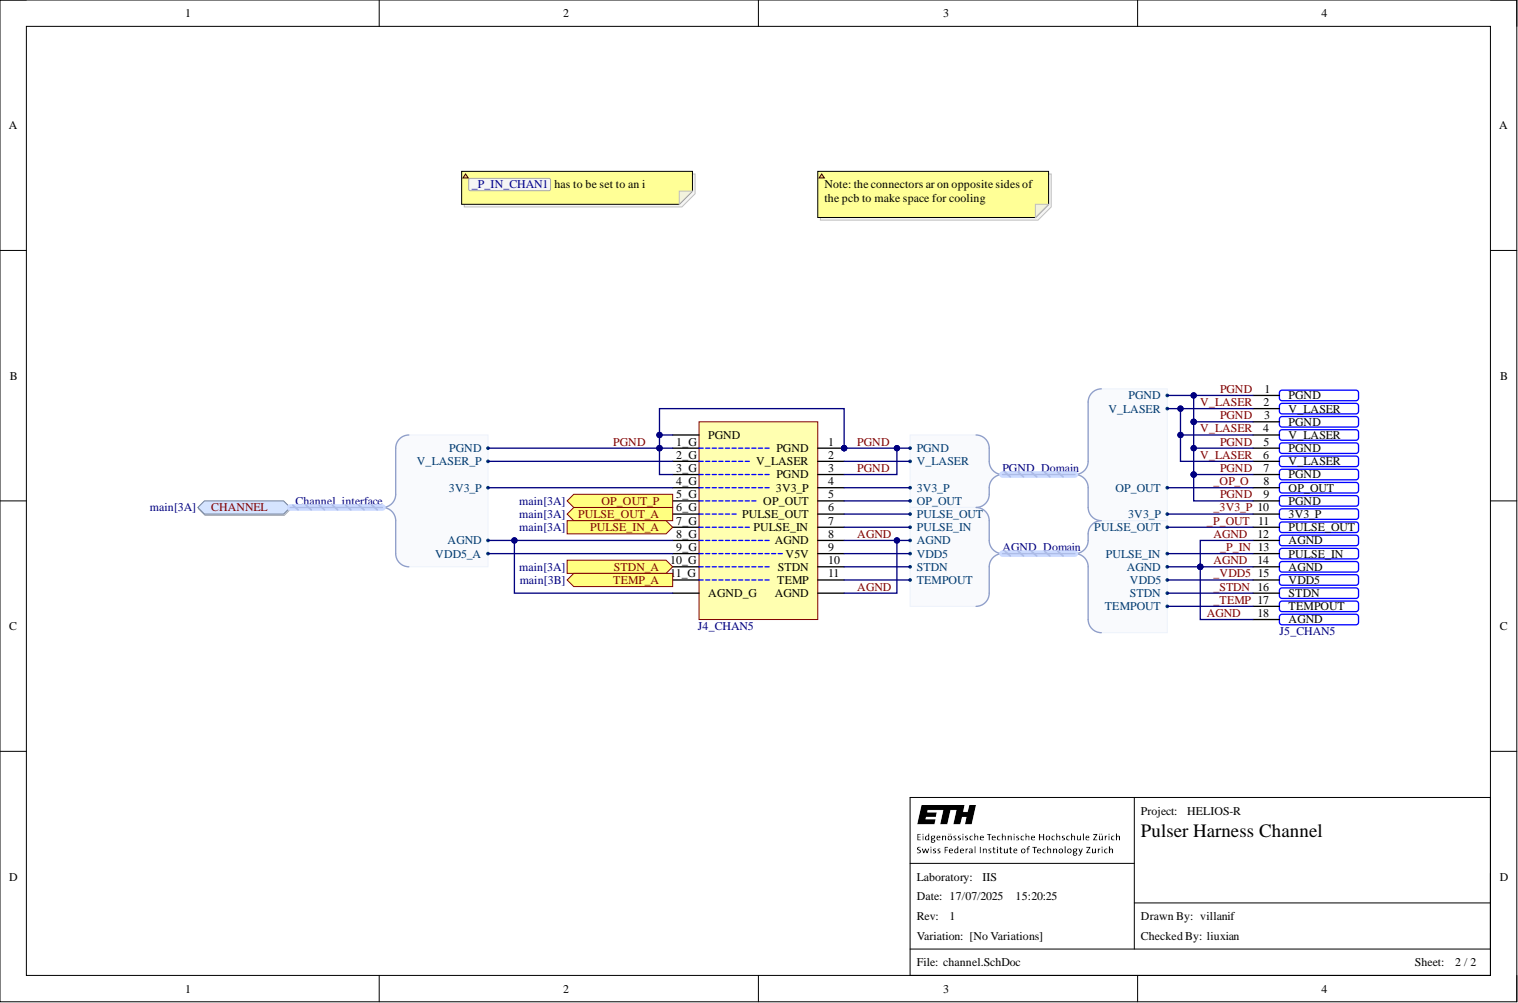
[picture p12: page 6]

_P_IN_CHAN1 has to be set to an i

Note: the connectors ar on opposite sides of
the pcb to make space for cooling

PGND

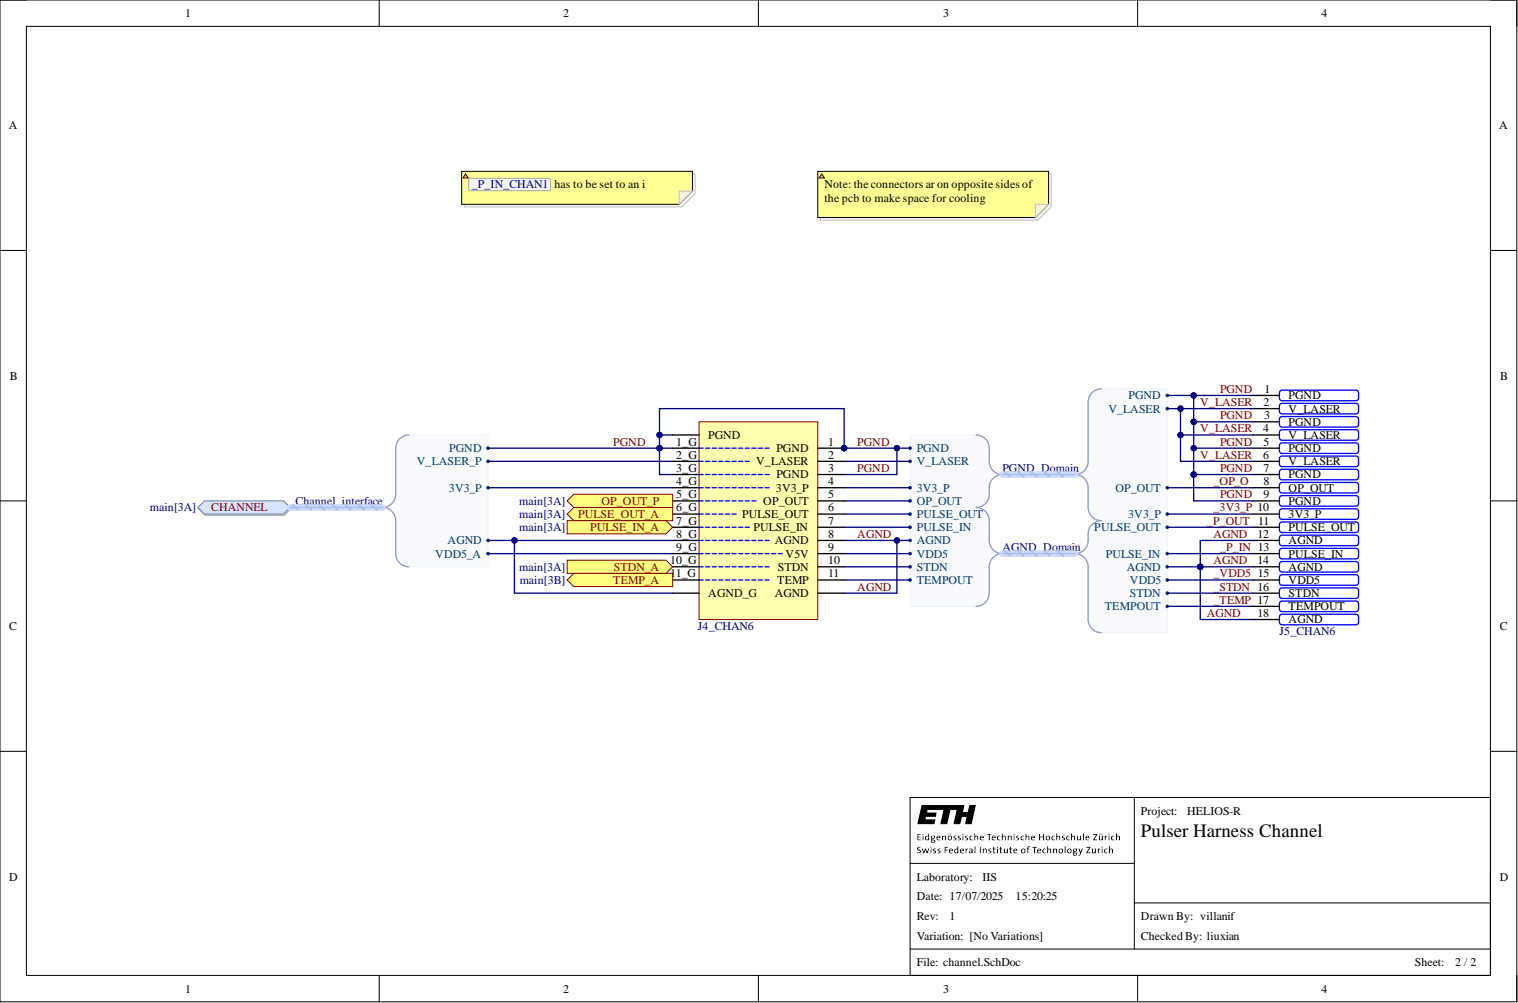
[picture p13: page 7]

_P_IN_CHAN1 has to be set to an i

Note: the connectors ar on opposite sides of
the pcb to make space for cooling

PGND


_P_IN_CHAN1 has to be set to an i

Note: the connectors ar on opposite sides of
the pcb to make space for cooling

PGND


_P_IN_CHAN1 has to be set to an i

Note: the connectors ar on opposite sides of
the pcb to make space for cooling

PGND


1 0

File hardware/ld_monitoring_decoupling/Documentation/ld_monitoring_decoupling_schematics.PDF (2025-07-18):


Requirements for digital isolator:
min pulse (unshortened) is 100 ns, max pulse 250ns
Specifications might be exceeded without causing extra
damage

power consumption of the whole board <10 mA
1 global to isolated high speed (PULSE)
1 global to isolated low speed (STDN)
Optional: 1 high-speed isolated to global (PULSEOUT)

Project: HELIOS-R
LD Monitoring and Decoupling

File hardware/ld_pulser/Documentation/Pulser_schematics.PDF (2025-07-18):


2 | V _ L ASE R


Mosfetsource is ground star point. Provide sufficient external
isolation where necessary to prevent ground loops. every AGND
domain should be isolated indipendently

The frontend pcb for the pulser module
Has to be used together with a controller board
Pulses 4 laser modules with 320 A and 20-24 V
Do not pulse longer than 150 ns

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

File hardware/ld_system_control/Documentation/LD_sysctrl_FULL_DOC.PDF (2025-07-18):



Project: HELIOS-R
LD Pulser - Layout Sheet


View from Top side (Scale 2:1)

Project: HELIOS-R
LD Pulser - Assembly Sheet


Drill View vias top-bottom (Scale 2:1)

Drill Table - top to bottom

Symbol | Count | Hole Size | Plated | Drill Layer Pair | Via / Pad

319 | 0.30mm | Plated | Top Layer - Bottom Layer | Via
46 | 1.02mm | Plated | Top Layer - Bottom Layer | Pad
6 | 1.10mm | Plated | Top Layer - Bottom Layer | Pad
2 | 1.10mm | Plated | Top Layer - Bottom Layer | Pad

Project: HELIOS-R LD Pulser - Manufacturing Sheet

Top Layer - Bottom Layer

16 | 1.60mm | Plated | Top Layer - Bottom Layer | Pad

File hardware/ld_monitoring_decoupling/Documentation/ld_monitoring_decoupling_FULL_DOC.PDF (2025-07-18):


Requirements for digital isolator:
min pulse (unshortened) is 100 ns, max pulse 250ns
Specifications might be exceeded without causing extra
damage

power consumption of the whole board <10 mA
1 global to isolated high speed (PULSE)
1 global to isolated low speed (STDN)
Optional: 1 high-speed isolated to global (PULSEOUT)

Project: HELIOS-R
LD Monitoring and Decoupling


Project: HELIOS-R
LD Pulser Driver - Layout


Project: HELIOS-R
LD Pulser Driver - Layout


Notes:
- Number on assembly view = line # of component
- Pin 1 is indicated by the black dot for each component
- Smallest components: 0201

Line # | Designator | Quantity | Description | Manufacturer Part Number 1
1 | C1, C2, C9, C10 | 4 | CAP CER 0.1UF 35V X5R 0201 | GRM033R6YA104ME14D
2 | C3, C8, C14, C15 | 4 | CAP CER 4.7UF 50V X6S 0805 | GRM21BC81H475KE11K
3 | C4, C5, C6, C7, C13 | 5 | CAP LOW L CER 1UF 6.3V X7T 0204 | LLL152D70J105ME01D
4 | C11, C12 | 2 | CAP CER 20PF 50V C0G/NP0 0402 | GCM1555C1H200FA16D

8 | R4, R5 | 2 | RES SMD 0OHM 0.1% 1/20W 0201 | ERJ-1GN0R00C
9 | R6 | 1 | RES 0.033 OHM 1% 1/4W 0603
10 | R7, R8 | 2 | RES SMD 0OHM 1/10W 0402 | ERJ-S020R00X
11 | R9, R10 | 2 | RES SMD 4.99 kOHM 1% 1/20W 0201 | ERJ-1GNF4991C
12 | R11 | 1 | RES SMD 24 OHM 1% 1/20W 0201 | ERJ-1GNF24R0C
13 | U1 | 1 | IC Inamp high-side current monitor | INA139NA/3K
14 | U2 | 1 | IC Digital Isolator, 2CH | MAX22291CASA/V+
15 | U3 | 1 | IC Single 2-Input Positive-AND Gate, YZP0005ADAD, LARGE T&R | SN74LVC1G08YZPR

Project: HELIOS-R
LD Pulser - Assembly Sheet


High-frequency isolated domain

Project: HELIOS-R
LD Pulser Driver - Connectors


Project: HELIOS-R
LD Pulser Driver - Manufacturing


Drill Drawing View (Scale 8:1)

Drill Table - top to bottom

Symbol | Count | Hole Size | Plated | Drill Layer Pair | Via / Pad

54 | 0.20mm | Plated | Top Layer - Bottom Layer | Via
22 | 0.60mm | Plated | Top Layer - Bottom Layer | Pad
76 Total

Project: HELIOS-R
LD Pulser Driver - Manufacturing

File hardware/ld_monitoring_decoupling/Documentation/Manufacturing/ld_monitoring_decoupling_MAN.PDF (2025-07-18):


Project: HELIOS-R
LD Pulser Driver - Manufacturing


Drill Table - top to bottom

Symbol | Count | Hole Size | Plated | Drill Layer Pair | Via / Pad

54 | 0.20mm | Plated | Top Layer - Bottom Layer | Via
22 | 0.60mm | Plated | Top Layer - Bottom Layer | Pad
76 Total

Drill View vias top-bottom (Scale 8:1)

Project: HELIOS-R
LD Pulser Driver - Manufacturing

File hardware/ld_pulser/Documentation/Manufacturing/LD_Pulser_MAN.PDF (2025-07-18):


Via Type Type 7 (Scale 16:1)

Through Hole Vias: filled with Resin, Via in Pad, Capped
Microvias: Filled with conductive material, Capped

Project: HELIOS-R
LD Pulser - Manufacturing Sheet


Drill View vias top-bottom (Scale 6:1)

Drill Table - top to bottom

278 | 0.20mm | Plated | Top Layer - Bottom Layer | Via
278 Total

Drill Table - microvias - top layer

Symbol | Count | Hole Size | Plated | Drill Layer Pair | Via / Pad

180 | 0.15mm | Plated | [UVIA] Top Layer - Int1(GND) | Via
59 | 0.20mm | Plated | [UVIA] Top Layer - Int1(GND) | Via
239 Total

Drill Table - microvias - bottom layer

182 | 0.15mm | Plated | [UVIA] Int4(GND) - Bottom Layer | Via
45 | 0.20mm | Plated | [UVIA] Int4(GND) - Bottom Layer | Via
227 Total

Project: HELIOS-R
LD Pulser - Manufacturing Sheet


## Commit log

2025-07-17 initial release commit
    [LD_panel_monitoring_module.PcbDoc, Pulser.SchDoc, channel.SchDoc, ld_harness.PrjPcb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]
2025-07-18 refactor monitoring_decoupling document
    [ld_monitoring_decoupling.PcbDoc, ld_monitoring_decoupling.SchDoc, main.SchDoc]
2025-07-18 add gerber files
    [Bill of Materials-BOM.xlsx, Bill of Materials-ld_p_testboard.xlsx, Bill of Materials-ld_system_control.xlsx, Bill of Materials-pulser(fabrication).xlsx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]
